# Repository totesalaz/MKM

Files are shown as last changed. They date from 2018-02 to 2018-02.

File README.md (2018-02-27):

# Motorized Kinematic Mount (MKM)
Here we present a simple, flexible and cost-effective system that combines 3D printed components, an Arduino board, and simple electronics to automatize a vast majority of kinematic mounts available on the market.

<p align="center">
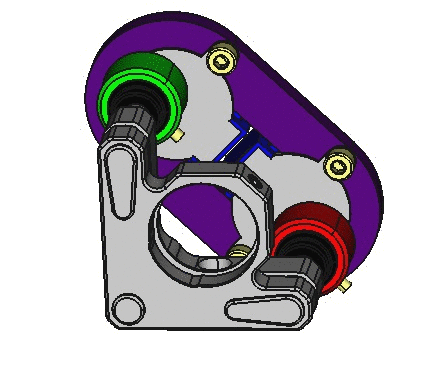
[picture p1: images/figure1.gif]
  
  <figcaption><bolf>Figure 1. Fully assembled Motorized Kinematic Mount.</bold></figcaption>
</p>

The simplicity of the system relies on the components used to implement it. As can be seen on the gif figure, the system is composed of a 3D printed plate that supports two motors whose shafts are aligned with the knobs used to tip and tilt the plane of a kinematic mount that supports the optics. The cylindrical adapter used to couple the shaft to the knob is also 3D printed. To control the motors, an Arduino MEGA connected to a sensor shield is used. 

Regarding flexibility, the hardware and software of the system can be easily modified according to the user needs. From the hardware side, since the 3D printed components that couple the system to the kinematic mount were parametrically designed using [FreeCAD 0.16](https://www.freecadweb.org/), the system is highly tunable by changing a few parameters on a spreadsheet. Similarly from the software side, the Arduino code is well documented and some usage examples are provided in the *.ino file. 

Last but not least, the cost of the system is directly related to its simplicity. As a reference, the total cost of fabricating a system composed of four stepper motors that can be used to control two kinematic mounts is around 50 EUR. As a result the system developed compares favourably with respect to commercial alternatives that can be roughly between 5 to 10 times more expensive. However, a word of caution should be added here. Since the system keeps track of the number of steps given by the stepper motor of each channel to estimate its current position, some inaccuracies may appear due to the hysteresis present on the stepper motors. Therefore, the usefulness of the system presented here depends on the application. Fortunately, from our experience in the laboratory, we have found that the system is suitable for a wealth of applications ranging from teaching to research laboratories.

## List of materials
To motorize a kinematic mount, the following materials are required. It is assumed that the Arduino MEGA and the sensor shield have been already acquired and the file **Motorized_Kinematic_Mount.ino** has been succesfully uploaded.

| Component | Quantity |
|--------------|--------------|
| Parametric plaque (parametric_plaque.FCStd) | 1 |
| Knob adapter (knob_adapter.FCSTD) | 2 |
| M3 screw | 4 |
| Stepper Motor (28BYJ-48) | 2 |
| Dupont cable (patch of 6 cables) | 2 |

## Hardware Implementation
A single unit of the system, capable of controlling the tip and tilt of a kinematic mount, is composed of two stepper motors (28BYJ-48) attached to the 3D printed plaque that aligns the knobs of the kinematic mount with the axis of the motors. The axis are coupled to the knobs using a 3D printed knob adapter. The motor drivers are connected to an Arduino MEGA sensor shield (attached to and Arduino MEGA) using Dupont wire jumper cables. 

<p align="center">
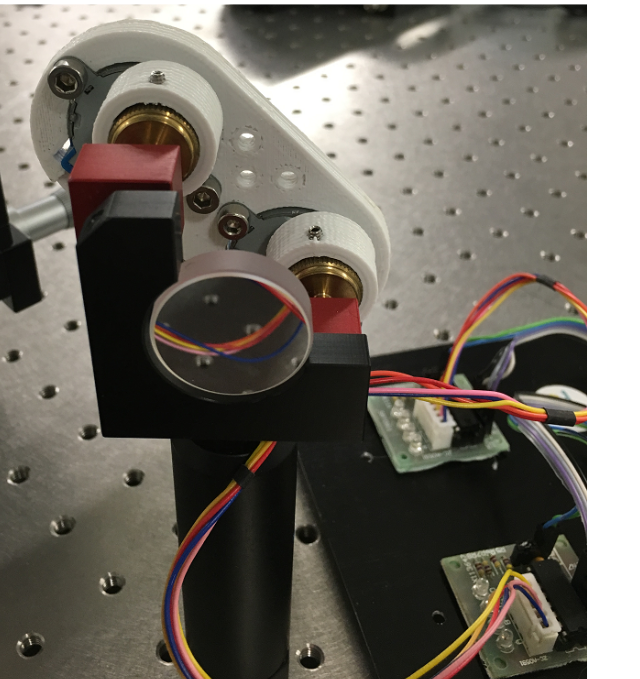
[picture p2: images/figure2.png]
  
  <figcaption><bolf>Figure 2. Example of implementation for a Radiant Dyes kinematic mount.</bold></figcaption>
</p>

Regarding the stepper motor used, the 28BYJ-48 is a very cheap motor that requires five wires for its connection to the driver circuit (reference ULN2003). The motor can operate in the voltage range 5V to 12V and theoretically it gives 4096 steps per one turn. This number comes from the fact that the internal stepper motor that requires 64 steps to give a complete turn is connected to a set of gears that provide a reduction ratio of 1/64. As a result the 28BYJ-48 requires 64x64=4096 steps to complete a full turn. 

The following figure provides a connection diagram for two stepper motors. Each channel is composed of a stepper motor 28BYJ-48, driver electronics and a Dupont cable patch with six wires. Given the number of output pins available on the Arduino sensor shield, the board can be used to control up to five kinematic mounts simultaneously as shown in panel (b). In other terms, the shield can connect up to ten motors simultaneously (**Attention!** connecting more than four motors may require an external power supply).

<p align="center">
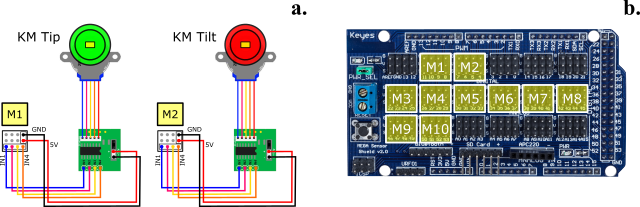
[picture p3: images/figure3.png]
  
  <figcaption><bold>Figure 3. Motorized Kinematic Mount connection diagram</bold></figcaption>
</p>

Since the 3D printed components that couple the stepper motors to the kinematic mount were designed using FreeCAD 0.16, the distance between motor axis on the plate (L), and the inner diameter (D) and height (H) on the knob adapters can be easily modified using a spreadsheet. To attach the motors to the PLA plate, four M4 screws are required, whereas two M3 grub screws are used to secure the knobs to the knob adapters.

<p align="center">
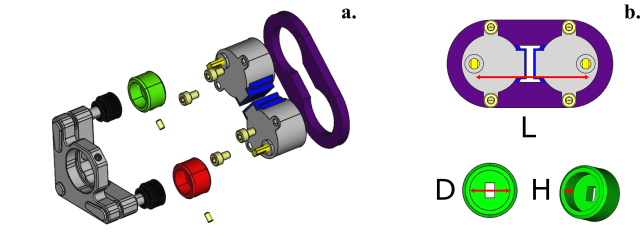
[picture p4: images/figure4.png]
  
</p>

The following table provides information on the parameters used for customizing the plate and the knob adapter to fit into four different types of kinematic mounts. 

Parameter | Variable | Thorlabs KM100 | Radiant Dyes | Liop-tec |
--- | --- | --- | --- | ---
Axis distance (mm) | L | 53.3 | 43.8 | 49 
Diameter (mm) | D | 14.8 | 16.6 | TBD 
Height (mm) | H | 8.0 | 6.0 | TBD

## Software Implementation
In order to provide flexibility and simplicity from the software perspective, each motor can be controlled independently by sending a simple instruction defined by a command table through the serial port. This approach enables the use of simple RS232 terminals such as [Termite](https://www.compuphase.com/software_termite.htm) and avoids the usage of additional drivers (complex and memory hungry) besides the drivers required by the Arduino board.

A command table is a dictionary of instructions that can be divided into two categories: commands and queries. The first category corresponds to a direct order such as "move stepper motor connected to port 3, half-turn". The second type of command is used to ask information to the device about its status; for example the state of a digital variable, the value of a given counter or the identification string that contains relevant information about the device and its manufacturer. 

The following table shows the complete list of commands used to control and retrieve information of the status of each motor connected to the Arduino board. Since the status of each motor is determined by a variable that keeps track of the number of steps given by the motor, it is assumed a one-to-one correspondence between the number of steps defined by software and the number of steps given by the axis of the internal stepper motor. A step given on the clock-wise direction adds one unit to the counter; a step given on the counter-clock-wise direction subtracts a unit. To keep the current status of each motor over time, each counter is stored in the non volatile section of the Arduino (EEPROM memory) so that all the information is available even though the Arduino board is powered off.

| Command | Description |
|----------------|----------------|
| STPM:N:ABS:X | move STePper Motor N to ABSolute position X (in steps) |
| STPM:N:REL:X | move STePper Motor N, RELative to current position |
| STPM:N:RST   | ReSeT STePper Motor N counter to 0 |
| STPM:N:VEL:X | set STePper Motor N, VELocity to X, where X (1 fast / 10 slow) |
| STPM:N:ST?   | retrieve motor N current STatus (position, velocity, state) |
|              | velocity -> (1 fast / 10 slow) |
|              | state -> (0 stop / 1 moving) |
| STOP         | emergency stop. Press reset button to restart |

Since the control method is based on a command table, there are many alternatives to implement the software interface that controls the system. Depending on the application, the user may require to perform simple actions driven by simple commands, or a more elaborate sequence of tasks dependent on external signals or defined by an algorithm with temporal dependence. The former can be implemented by sending commands through the serial port using a serial communication terminal compatible with the RS232 standard such as Termite and the latter can be implemented using MATLAB or Python.

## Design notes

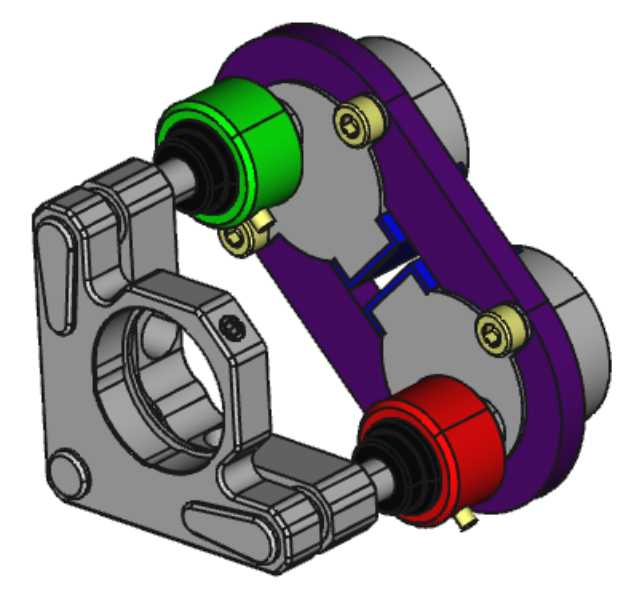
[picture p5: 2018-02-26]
images/figure1.png

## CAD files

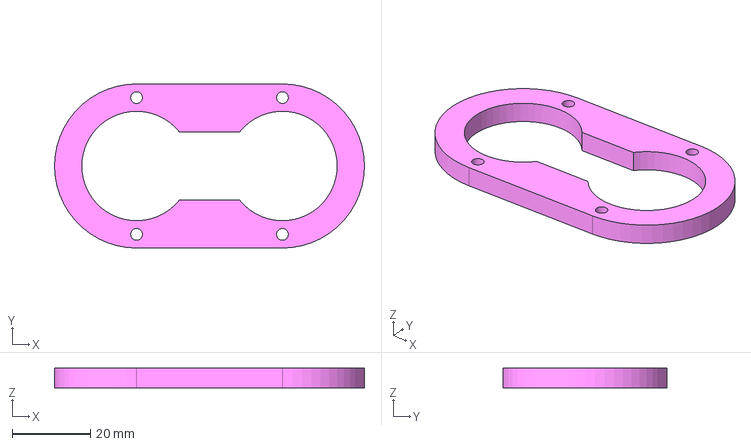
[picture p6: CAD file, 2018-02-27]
parametric_plaque.FCStd
79.3 x 42.0 x 5.00 mm

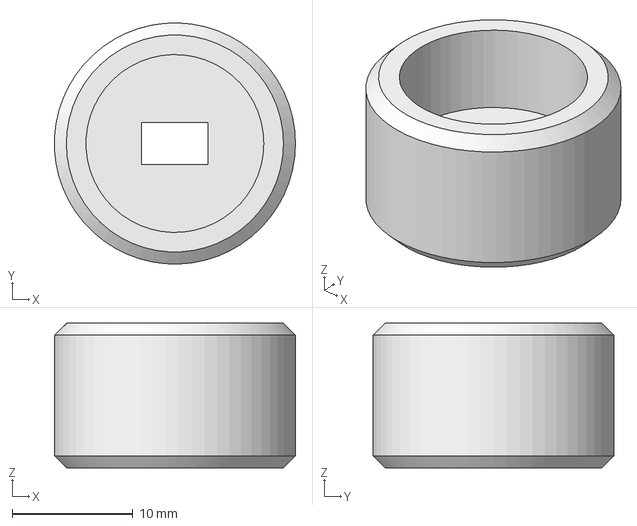
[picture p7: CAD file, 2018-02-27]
knob_adapter.FCStd
20.0 x 20.0 x 12.0 mm

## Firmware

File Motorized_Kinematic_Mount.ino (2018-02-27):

/*

  Filename: Motorized_Kinematic_Mount.ino
       
  Description: 
  Program that allows to control TEN stepper motors (28BYJ-48) connected to an 
  Arduino Mega sensor shield. The motors are connected to the following pins:
   
  motor1 -> 8, 9, 10, 11
  motor2 -> 4, 5, 6, 7
  motor3 -> 22, 23, 24, 25
  motor4 -> 26, 27, 28, 29
  motor5 -> 30, 31, 32, 33
  motor6 -> 34, 35, 36, 37
  motor7 -> 38, 39, 40, 41
  motor8 -> 42, 43, 44, 45 
  motor9 -> 46, 47, 48, 49
  motor10-> 50, 51, 52, 53
 
  The status of each motor and its state can be defined by means of the following set
  of commands:
  
  | Command       | Description                                                     |
  | STPM:N:ABS:X  | move STePper Motor N to ABSolute position X (in steps)          |
  | STPM:N:REL:X  | move STePper Motor N, RELative to current position              |
  | STPM:N:RST    | ReSeT STePper Motor N counter to 0                              |
  | STPM:N:VEL:X  | set STePper Motor N, VELocity to X, where X [1 fast | 10 slow]  |
  | STPM:N:ST?    | retrieve motor N current STatus (position, velocity, state)     |
  |               | velocity -> [1 fast | 10 slow]                                  |
  |               | state -> [0 stop | 1 moving]                                    |
  | STOP          | emergency stop. Press reset button to restart                   |
  
  Note: for a standard 28BYJ-48 stepper motor, one turn takes 4096 steps.
    
  Usage example: open Arduino serial console and write
  STPM:1:REL:4096 (one turn corresponds to 4096 steps)
  STPM:1:ST?
  >> 4096:1:0
        
  Created by Luis José Salazar-Serrano
  http://opensourcelab.salazarserrano.com
  totesalaz@gmail.com
  Created  8 / August /2016
  Modified 6 / October / 2016
  Version 2.0
  
  Code based on the following works
  https://learn.adafruit.com/multi-tasking-the-arduino-part-1
  https://arduino-info.wikispaces.com/SmallSteppers
  https://www.arduino.cc/en/Tutorial/SerialEvent
  
*/

#include <EEPROM.h>

const byte interruptPin = 21; // attach "panic button" to external interrupt pin

String commandString = ""; // a string to hold incoming data
boolean stringComplete = false; // whether the string is complete

// function that determines sign +/- of argument
int sign(int x) { 
  return (x>0) - (x<0); 
}

typedef struct {
  
  int cnt;
  int vel;
  boolean state;

} motorStatus;

class StepperMotor
{  
  int motorPin1;  //blue cable stepper motor 28BYJ-48
  int motorPin2;  //pink cable stepper motor 28BYJ-48
  int motorPin3;  //yellow cable stepper motor 28BYJ-48
  int motorPin4;  //orange cable stepper motor 28BYJ-48
  int memoryPos;  //EEPROM memory position
  
  int newPosition;
 
  unsigned int currentSpeed; 
  unsigned long previousMillis;
  
  motorStatus array;
 
  int motorSequence[8];
  
  //Constructor
  public: 
  StepperMotor(int bluePin, int pinkPin, int yellowPin, int orangePin, int memorySlot)
  {
    motorPin1 = bluePin;
    pinMode(motorPin1,OUTPUT);
    motorPin2 = pinkPin;
    pinMode(motorPin2,OUTPUT);
    motorPin3 = yellowPin;
    pinMode(motorPin3,OUTPUT);
    motorPin4 = orangePin;
    pinMode(motorPin4,OUTPUT);
    memoryPos = memorySlot;
       
//    array.cnt = 0;
    EEPROM.get(memoryPos*sizeof(int), array.cnt); 

    array.vel = 1;
    array.state = false;
//    newPosition = 0;
    EEPROM.get(memoryPos*sizeof(int), newPosition);   
    previousMillis = 0;

    motorSequence[0] = B1000;
    motorSequence[1] = B1100;
    motorSequence[2] = B0100;
    motorSequence[3] = B0110;
    motorSequence[4] = B0010;
    motorSequence[5] = B0011;
    motorSequence[6] = B0001;
    motorSequence[7] = B1001;    
}
  
  void Update()
  {
            
    unsigned long currentMillis = millis();
    if((currentMillis-previousMillis >= abs(array.vel)) && (newPosition != array.cnt)){
              
      previousMillis = currentMillis;
      array.cnt += sign(newPosition-array.cnt);     
//      EEPROM.put(motorPin1*sizeof(int), array.cnt);  // don't use it! 
      
      digitalWrite(motorPin1,bitRead(motorSequence[((array.cnt % 8) + 8) % 8],0));
      digitalWrite(motorPin2,bitRead(motorSequence[((array.cnt % 8) + 8) % 8],1));
      digitalWrite(motorPin3,bitRead(motorSequence[((array.cnt % 8) + 8) % 8],2));
      digitalWrite(motorPin4,bitRead(motorSequence[((array.cnt % 8) + 8) % 8],3));                 

      if(newPosition == array.cnt){        
        EEPROM.put(memoryPos*sizeof(int), array.cnt);  
        array.state = false;
        digitalWrite(motorPin1,0);
        digitalWrite(motorPin2,0);
        digitalWrite(motorPin3,0);
        digitalWrite(motorPin4,0);                 
      }else{
        array.state = true; // motor is moving
      }

    }
  }

  void relMove(int steps)
  { 
    newPosition = array.cnt + steps;
  }

  void absMove(int steps)
  { 
    newPosition = steps;
  }

  void velMove(int velocity)
  { 
    array.vel = velocity;
  }

  void Status(){
//    EEPROM.get(memoryPos*sizeof(int), array.cnt);
    Serial.println(String(array.cnt)+":"+String(array.vel)+":"+String(array.state));    
  }
  
  void resetCnt()
  { 
    array.cnt = 0;
    newPosition = 0;
    EEPROM.put(memoryPos*sizeof(int), array.cnt);  
  }
  
  void emerStop()
  { 
    EEPROM.put(memoryPos*sizeof(int), array.cnt);  
  }

};

StepperMotor motor1(8,9,10,11,0);
StepperMotor motor2(4,5,6,7,1);  
StepperMotor motor3(22,23,24,25,2);
StepperMotor motor4(26,27,28,29,3);
StepperMotor motor5(30,31,32,33,4);
StepperMotor motor6(34,35,36,37,5);
StepperMotor motor7(38,39,40,41,6);
StepperMotor motor8(42,43,44,45,7);
StepperMotor motor9(46,47,48,49,8);
StepperMotor motor10(50,51,52,53,9);

void setup()
{
  Serial.begin(9600);
  /* // uncomment to initialize EEPROM memory to 0
  EEPROM.put(0*sizeof(int), 0);
  EEPROM.put(1*sizeof(int), 0);  
  EEPROM.put(2*sizeof(int), 0);  
  EEPROM.put(3*sizeof(int), 0);  
  // */  
  attachInterrupt(digitalPinToInterrupt(interruptPin), emergency, CHANGE);
}

void loop()
{

  motor1.Update();
  motor2.Update();
  motor3.Update();
  motor4.Update();
  motor5.Update();
  motor6.Update();
  motor7.Update();
  motor8.Update();
  motor9.Update();
  motor10.Update();
    
}


/*
SerialEvent occurs whenever a new data comes in the
hardware serial RX. This routine is run between each
time loop() runs, so using delay inside loop can delay
response. Multiple bytes of data may be available.

Function taken from:
https://www.arduino.cc/en/Tutorial/SerialEvent
*/

void serialEvent() {

while (Serial.available()) {
// get the new byte:
char inChar = (char)Serial.read();

// add it to the inputString:
if (inChar != '\n')
commandString += inChar;
//Serial.println(commandString);

// if the incoming character is a newline, set a flag
// so the main loop can do something about it:
if (inChar == '\n'){
  commandString.toUpperCase();
//  Serial.println(commandString);
  stringComplete = true;
}
}

if(stringComplete){
//  Serial.println(commandString.substring(0,11));
//  Serial.println(String(commandString.substring(11).toInt()+10));

  // motor1
  if(commandString.substring(0,11) == "STPM:1:REL:"){  
    motor1.relMove(commandString.substring(11).toInt());
  }

  if(commandString.substring(0,11) == "STPM:1:ABS:"){   
    motor1.absMove(commandString.substring(11).toInt());
  }

  if(commandString.substring(0,11) == "STPM:1:VEL:"){  
    motor1.velMove(commandString.substring(11).toInt());
  }

  if(commandString == "STPM:1:RST"){  
    motor1.resetCnt();
  }

  if(commandString == "STPM:1:ST?"){
    motor1.Status();
  }

  // motor2
  if(commandString.substring(0,11) == "STPM:2:REL:"){  
    motor2.relMove(commandString.substring(11).toInt());
  }

  if(commandString.substring(0,11) == "STPM:2:ABS:"){   
    motor2.absMove(commandString.substring(11).toInt());
  }

  if(commandString.substring(0,11) == "STPM:2:VEL:"){  
    motor2.velMove(commandString.substring(11).toInt());
  }

  if(commandString == "STPM:2:RST"){  
    motor2.resetCnt();
  }

  if(commandString == "STPM:2:ST?"){
    motor2.Status();
  }

  // motor3
  if(commandString.substring(0,11) == "STPM:3:REL:"){  
    motor3.relMove(commandString.substring(11).toInt());
  }

  if(commandString.substring(0,11) == "STPM:3:ABS:"){   
    motor3.absMove(commandString.substring(11).toInt());
  }

  if(commandString.substring(0,11) == "STPM:3:VEL:"){  
    motor3.velMove(commandString.substring(11).toInt());
  }

  if(commandString == "STPM:3:RST"){  
    motor3.resetCnt();
  }

  if(commandString == "STPM:3:ST?"){
    motor3.Status();
  } // end motor 3*/
  
  // motor4
  if(commandString.substring(0,11) == "STPM:4:REL:"){  
    motor4.relMove(commandString.substring(11).toInt());
  }

  if(commandString.substring(0,11) == "STPM:4:ABS:"){   
    motor4.absMove(commandString.substring(11).toInt());
  }

  if(commandString.substring(0,11) == "STPM:4:VEL:"){  
    motor4.velMove(commandString.substring(11).toInt());
  }

  if(commandString == "STPM:4:RST"){  
    motor4.resetCnt();
  }

  if(commandString == "STPM:4:ST?"){
    motor4.Status();
  } // end motor 4*/
  
  // motor5
  if(commandString.substring(0,11) == "STPM:5:REL:"){  
    motor5.relMove(commandString.substring(11).toInt());
  }

  if(commandString.substring(0,11) == "STPM:5:ABS:"){   
    motor5.absMove(commandString.substring(11).toInt());
  }

  if(commandString.substring(0,11) == "STPM:5:VEL:"){  
    motor5.velMove(commandString.substring(11).toInt());
  }

  if(commandString == "STPM:5:RST"){  
    motor5.resetCnt();
  }

  if(commandString == "STPM:5:ST?"){
    motor5.Status();
  } // end motor 5*/

  // motor6
  if(commandString.substring(0,11) == "STPM:6:REL:"){  
    motor6.relMove(commandString.substring(11).toInt());
  }

  if(commandString.substring(0,11) == "STPM:6:ABS:"){   
    motor6.absMove(commandString.substring(11).toInt());
  }

  if(commandString.substring(0,11) == "STPM:6:VEL:"){  
    motor6.velMove(commandString.substring(11).toInt());
  }

  if(commandString == "STPM:6:RST"){  
    motor6.resetCnt();
  }

  if(commandString == "STPM:6:ST?"){
    motor6.Status();
  } // end motor 6*/

  // motor7
  if(commandString.substring(0,11) == "STPM:7:REL:"){  
    motor7.relMove(commandString.substring(11).toInt());
  }

  if(commandString.substring(0,11) == "STPM:7:ABS:"){   
    motor7.absMove(commandString.substring(11).toInt());
  }

  if(commandString.substring(0,11) == "STPM:7:VEL:"){  
    motor7.velMove(commandString.substring(11).toInt());
  }

  if(commandString == "STPM:7:RST"){  
    motor7.resetCnt();
  }

  if(commandString == "STPM:7:ST?"){
    motor7.Status();
  } // end motor 7*/

  // motor8
  if(commandString.substring(0,11) == "STPM:8:REL:"){  
    motor8.relMove(commandString.substring(11).toInt());
  }

  if(commandString.substring(0,11) == "STPM:8:ABS:"){   
    motor8.absMove(commandString.substring(11).toInt());
  }

  if(commandString.substring(0,11) == "STPM:8:VEL:"){  
    motor8.velMove(commandString.substring(11).toInt());
  }

  if(commandString == "STPM:8:RST"){  
    motor8.resetCnt();
  }

  if(commandString == "STPM:8:ST?"){
    motor8.Status();
  } // end motor 8*/

  // motor9
  if(commandString.substring(0,11) == "STPM:9:REL:"){  
    motor9.relMove(commandString.substring(11).toInt());
  }

  if(commandString.substring(0,11) == "STPM:9:ABS:"){   
    motor9.absMove(commandString.substring(11).toInt());
  }

  if(commandString.substring(0,11) == "STPM:9:VEL:"){  
    motor9.velMove(commandString.substring(11).toInt());
  }

  if(commandString == "STPM:9:RST"){  
    motor9.resetCnt();
  }

  if(commandString == "STPM:9:ST?"){
    motor9.Status();
  } // end motor 9*/

  // motor10
  if(commandString.substring(0,12) == "STPM:10:REL:"){  
    motor10.relMove(commandString.substring(12).toInt());
  }

  if(commandString.substring(0,12) == "STPM:10:ABS:"){   
    motor10.absMove(commandString.substring(12).toInt());
  }
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
